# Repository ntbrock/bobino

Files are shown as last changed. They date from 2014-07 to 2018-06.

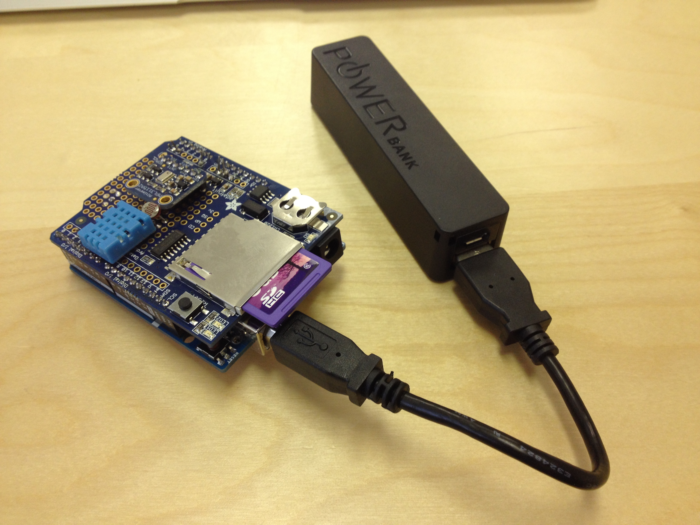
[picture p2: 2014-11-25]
Documentation/Bobino_Getting_Started_C.jpg

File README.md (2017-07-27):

BOBino
======

BOBino is an open source, educational, environmental sensor kit developed in Charleston, SC.  BOBino is built on Arduino open source hardware and intended to increase learning in electronics, data collection, and statistical analysis for students.

## Latest Release

Software: Version 1.6.1 (master)

Hardware: Version 1.6H (oshpark)

## Getting started quickly? 

Read the document "HOWTO Use Your Bobino.txt"

[HOWTO Use Your BOBino](https://github.com/ntbrock/bobino/blob/master/Documentation/HOWTO_Use_Your_Bobino.txt?raw=true)

## Announcing BOBino V1.6 at the South Carolina STEAM workshop

[View the July 2017 STEAM Workshop Presentation](https://github.com/ntbrock/bobino/blob/master/Documentation/BOBino%20STEAM%20Public%202017Jul.pptx?raw=true)

## Ready to compile the code yourself?

Latest codeset is in BOBino_Code_V1.6_2016Jun25, several Arduino libraries required: Narcoleptic, OneWire, DallasTemperature, RTClib

## Ready to build your own board?

Full schematic and PCB Layout avaialble on Autodesk's Circuits123

https://circuits.io/circuits/2376213-bobino-1-6h-environmental-data-logger-arduino-uno-half-shield

## Ready to order BOBino Kits or Arduino Shields for your classroom or workshop?

Email taylor.brockman@gmail.com with the Subject line: BOBino Order Information

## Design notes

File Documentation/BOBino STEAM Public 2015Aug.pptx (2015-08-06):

## BOBino 1.5 Environmental Logger Kit

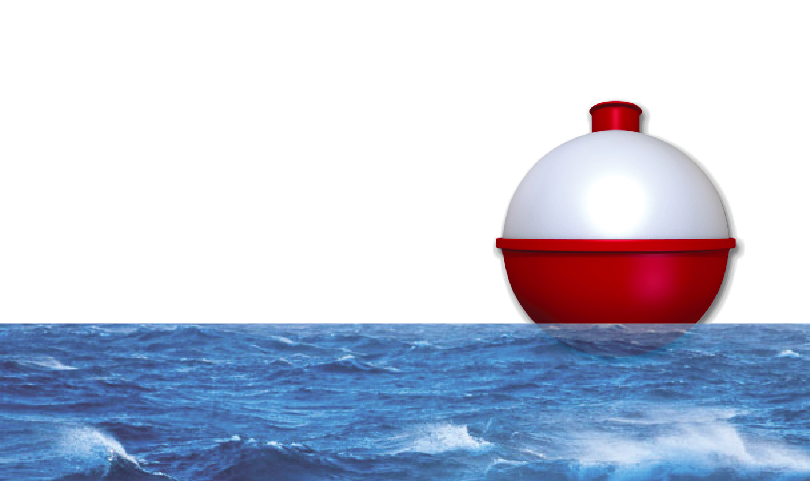
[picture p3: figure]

Taylor Brockman
2015-Aug-06

## NERD ALERT!

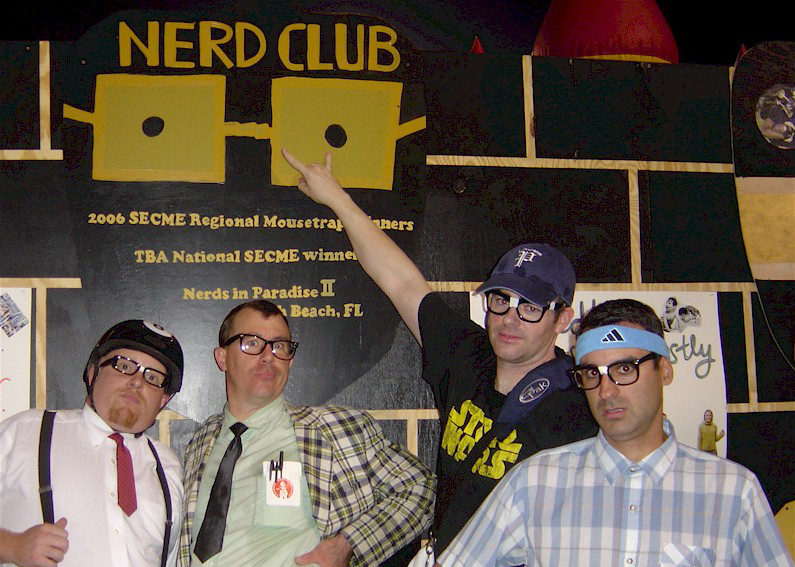
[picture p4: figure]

## NERD ALERT!

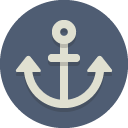
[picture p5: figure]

- New! Three Temperature Sensors!
- Open Source Code and Hardware
- Battery Powered, Durable, Cheap

## POP that tupperware open!

- STICKERS! (w/ QR Code)
- Arduino UNO plus “Shield”
- SD Memory Card
- 2 Temperature Sensor Wires
- Order Doesn’t Matter
- USB Battery and 2 Cables
- Power it up! Recharge anytime!

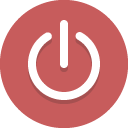
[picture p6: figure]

## We are LOGGIN The DATA!

- Default interval is 15 seconds
- Try covering up the Photo Sensor
- Try warming up a Temp Sensor
- Temp Sensors are submersible
- (Bubble Bubble Bubble)

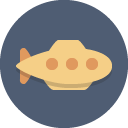
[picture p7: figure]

## Story Time & Fun pictureS

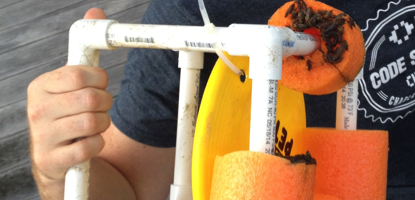
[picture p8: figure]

- Marina

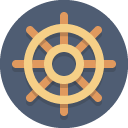
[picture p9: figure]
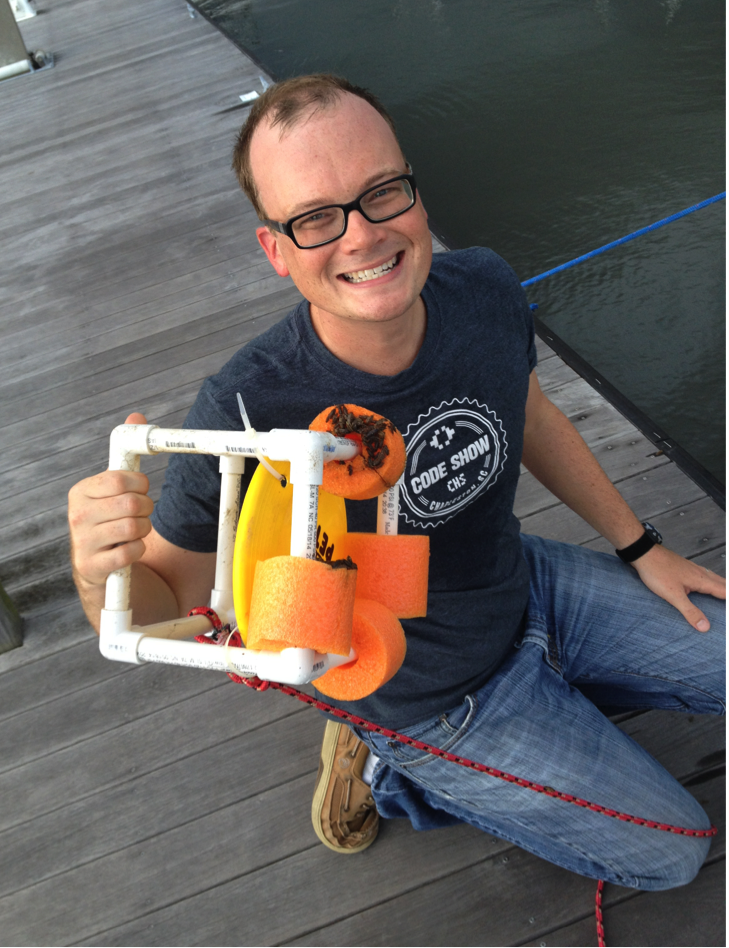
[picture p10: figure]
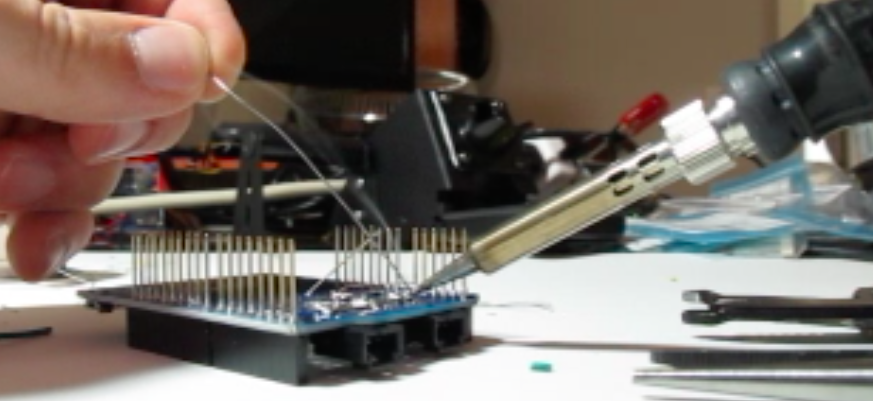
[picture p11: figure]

## Why BOBINO?

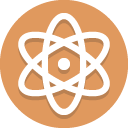
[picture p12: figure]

- Students need exposure to electronic data logging and statistical analysis and visualization.
- Commercial alternative is $1500
- Cha Ching!

## Let’s take a look ON OUR LAPTOPS

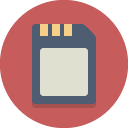
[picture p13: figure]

- SD Card can be plugged into any laptop or PC.
- DATA.CSV is “Comma Separated Values” that opens well in Excel.
- Change the Log Rate in CONFIG

## Let’s take a look ON OUR LAPTOPS

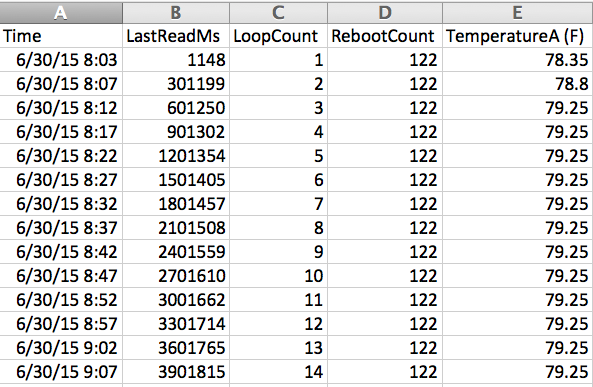
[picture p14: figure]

## Let’s take a look ON OUR LAPTOPS

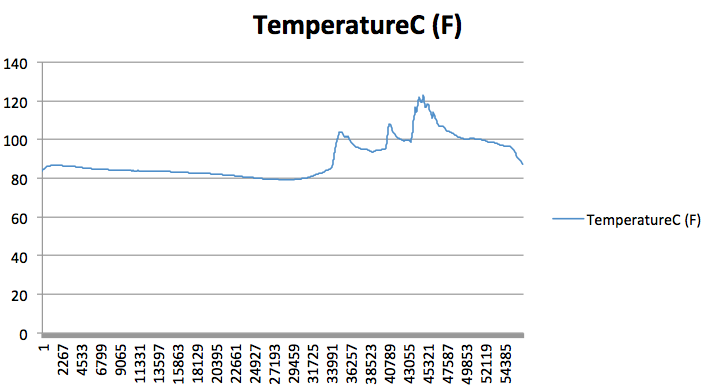
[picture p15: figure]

## Let’s take a look ON OUR LAPTOPS

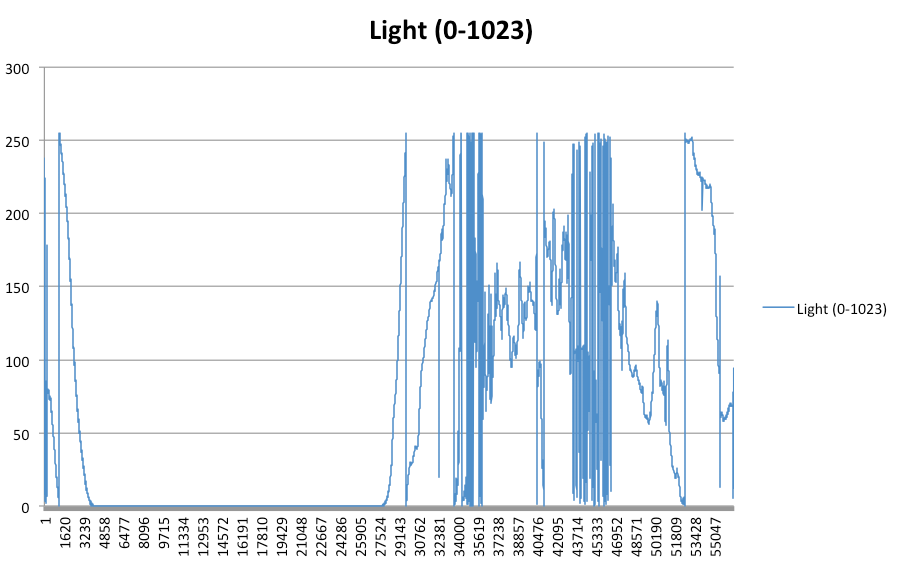
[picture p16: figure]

## Maybe it’s time to get a new fridge?

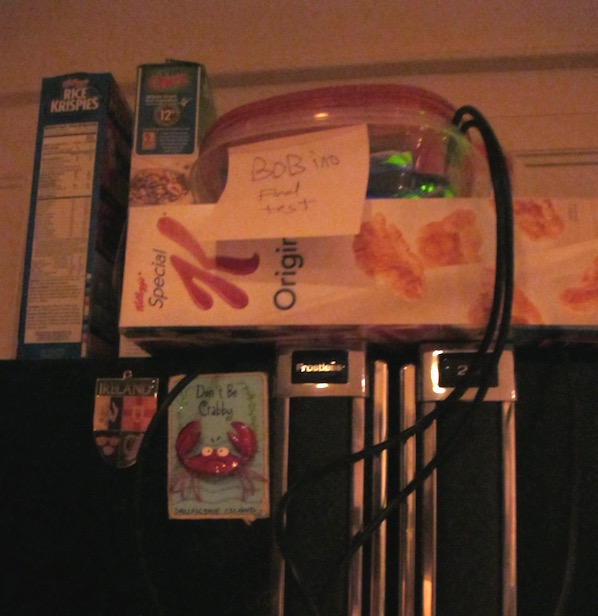
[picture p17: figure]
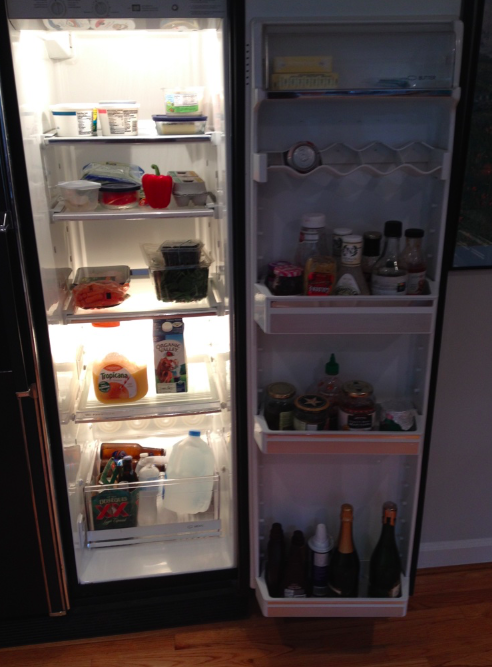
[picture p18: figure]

## Maybe it’s time to get a new fridge?

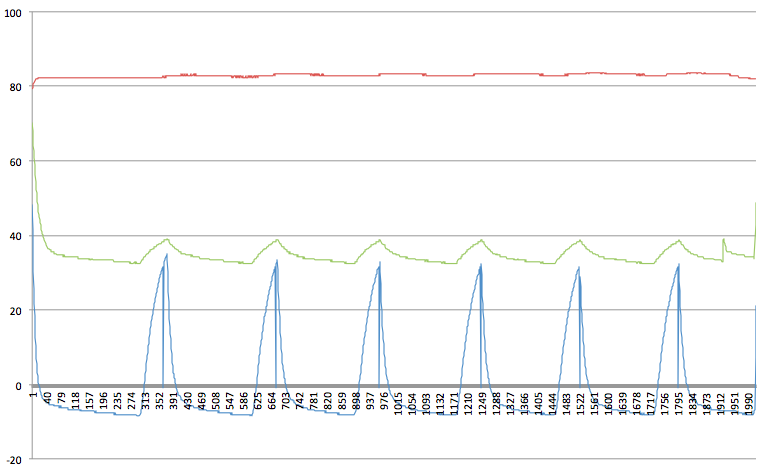
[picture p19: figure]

Morning Juice!

## Experiment IDEAS

- Refrigerator Performance
- Water Heating via Solar Radiance
- Air –vs– Water Temperature Diff
- Solar Day Length
- Cloud Cover –vs– Temperature
- Air Conditioner Thermostat Accuracy

## For the Experts

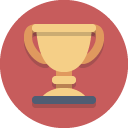
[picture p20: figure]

- All Source Code is available!
- Use the Arduino Programmer, Free Download!
- Add More Hardware, Change Shields, Increase the Battery Size
- Ocean or Sky is the limit!

## BOBino 1.5 Environmental Logger Kit

Taylor Brockman
2015-Aug-06

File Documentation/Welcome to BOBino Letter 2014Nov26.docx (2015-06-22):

November 26, 2014

Welcome to BOBino!

You are the proud custodian of a BOBino version 1.0 Arduino data sensor capture device, designed and assembled in Charleston, South Carolina, USA.

Your interest in the BOBino program helps create careers in Science, Technology, Engineering, Mathematics, and Software for bright, motivated students.

To get started with BoBinfo, assemble the unit, power it with the USB battery, then let it run for 5 minutes to collect readings! After that, remove the power, place the SD Card in any computer and open DATA.CSV in Microsoft Excel or a text editor to see all captured data points. Certain settings are configurable by editing the files in the CONFIG/ folder on the SD Card.

You can read a full getting started guide on the world wide web:

http://www.brockmanapprenticefoundation.org/Bobino/features.html

When you find a student who wants “more”, our Arduino source code is open, the BOBino can be reprogrammed and extended, and we are here to guide!

The Brockman Apprentice Foundation connects the brightest, hardest working students in the Carolinas to summer work / study programs. Learn more at:

http://www.brockmanapprenticefoundation.org/

Sincerely,
Taylor Brockman

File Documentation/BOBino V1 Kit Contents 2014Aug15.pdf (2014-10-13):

BOBino

V1 | | Taylor Brockman,

Maxwell

Tucker,

| | | | | Benson Robles
Kit
Contents | | 2014-‐Aug-‐15
Component | Vendor | Price
Each Qty | Ship
Rate Total | Description | URL
UNO | Adafruit | $24.95 | 5 | $0.00 $124.75 Arduino

Uno

R3

(Atmega328

-‐

assembled) http://www.adafruit.com/products/50 SD

Shield | Adafruit | $19.95 | 5 | $0.00 | $99.75 Adafruit

Assembled

Data

Logging

shield

for

Arduino[ID:1141] http://www.adafruit.com/product/1141 DHT11

Temp | Adafruit | $5.00 | 5 | $0.00 | $25.00 DHT11

basic

temperature-‐humidity

sensor

+

extras http://www.adafruit.com/products/386 Temp

Sensor | Adafruit | $9.95 | 5 | $0.00 | $49.75 MPL3115A2

-‐

I2C

Barometric

Pressure/Altitude/Temperature

Sensor[ID:1893] http://www.adafruit.com/product/1893 Photo

Sensor | Adafruit | $0.95 | 5 | $0.00 | $4.75 Photo cell (CdS

photoresistor)[ID:161] http://www.adafruit.com/product/161 USB

Battery | Adafruit | $14.95 | 5 | $0.00 | $74.75 USB Battery

Pack

-‐

2200

mAh

Capacity

-‐

5V

1A

Output http://www.adafruit.com/products/1959

SD

Card | Walmart | $4.83 | V7

2GB

SD

Card,

Secure

Digital

2

GB

Memory

Card

http://www.walmart.com/ip/V7-‐2GB-‐SD-‐Card-‐Secure-‐Digital-‐2-‐GB-‐Memory-‐Card/15172567

SD

Card

4G | Amazon | $5.75 | 6 | $0.00 | $34.50 SanDisk

SDSDB2L-‐004G-‐B35

http://www.amazon.com/gp/product/B002DS7NJI/ref=ox_sc_act_title_1?ie=UTF8&psc=1&smid=A3U5D1Y1DY YVD9
USB

B

Cable | Ebay | | | | 6" inch Black

USB

2.0

AB

Printer

-‐

Device

Cable

A-‐B
USB

AB

Cable | PCH
| Cables | $1.25 | 10 | $3.71 | $16.21 6 Inch USB

2.0

Type

A

Male

to

Type

B

Male

Cable

-‐

Black

http://www.pchcables.com/6inusb20tyma1.html

Tupperware | Publix | $1.00 | 5 | $0.00 | $5.00
Assembly
Labor | InnoLabs | $10 | 5 | $0.00 | $50.00

Total

Per

BOBino | | $96.89 | 5 | | $484.46 Grand

Total

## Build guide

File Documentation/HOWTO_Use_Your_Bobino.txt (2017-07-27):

HOWTO Use Your Bobino
BOBino V1.6 2017-Jul-27

0) BOBino kit contents:

   BOBino Purple Shield
   Data Logger Shield
   Arduino UNO Base
   USB Battery
   USB Square Cable
   USB Tiny Cable (for recharging battery)
   Two Temperature Probes
   Waterproof enclosure (Tupperware or Ziplock)

1) Assemble the unit:

A. Combine the shields: BOBino on top, Data Logger shield in the middle, Arduino UNO on the bottom.

B. Connect the temperature probes into Temp 1 and Temp 3, the plug will clip in with the clip facing up.

C. Place an SD Card Chip into Data Logger shield. If the card is blank, the first time BOBino boots up, it will write a new DATA.CSV file and create a CONFIG directory.

D. Plus the USB Power cable with the square end into the Arduino Uno, then plug the rectangular end into the USB Battery.

E. The unit takes approximately 5 seconds to boot up, initialize the SD card and begin taking readings!

F. Be sure that when you mount the BOBino into its waterproof case the photo sensor can see the sunlight and is not upside down.  I like to mount one temperature probe in the air and the other temperature probe into the water.

2) Let the Unit Run for 3 minutes 

The default sample rate is 1 reading per minute.

3) Unplug the Power and Read the SD card with a computer.

Remove the SD Card, and plug into any laptop or computer with an SD Card Reader.

On the disk, you will see a file called 'DATA.CSV', example contents:

Time,Temperature (F),Humidity,Pressure (in Hg),Light (Raw value 0-1023),Light (qualitative descriptor)
2000/1/1 0:0:0,74.19,47.00,30.05,316,bright
2014/9/5 16:27:0,74.75,47.00,30.05,323,bright
2014/9/5 16:27:59,74.64,47.00,30.05,321,bright
2014/9/5 16:28:59,74.75,47.00,30.05,319,bright
2014/9/5 16:29:59,74.97,47.00,30.06,338,bright
2014/9/5 16:30:59,75.09,47.00,30.05,326,bright

4) Reconfigure to your settings!

Adjust the settings on the Bobino is easy, simply edit the files in the CONFIG/ directory on the SD Card.

Edit The following files to set Configuration: 
   CONFIG/TEMP.TXT -- Set Temperature Units to F or C
   CONFIG/TIME.TXT -- Set Time Sleep Interval in minutes
   CONFIG/ALT.TXT -- Set Altitude Units and Activate
   CONFIG/RTCSET.TXT -- Set To the current calendar information to adjust system time.
   CONFIG/_RTCSET.TXT -- Example RTC File to make clock setting easy.

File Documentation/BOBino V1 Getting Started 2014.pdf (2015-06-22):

12/4/2014 | BOBino - Getting Started

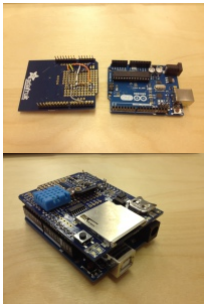
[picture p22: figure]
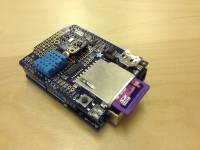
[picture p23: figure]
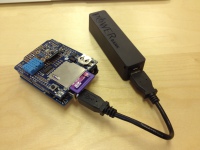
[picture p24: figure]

http://www.brockmanapprenticefoundation.org/Bobino/features.html | 1/3

# Getting Started with your BOBino

BOBino V1 2014-Sep-01

# 1) Assemble the BOBino:

A. The Sensor Shield attaches on top of the Arduino Uno

(Documentation/Bobino_GettingStarted_A.jpg) (http://www.brockmanapprenticefoundation.org/Bobino/Documentation/Bobino_GettingStarted_A.jpg)

(Documentation/Bobino_GettingStarted_A2.jpg) (http://www.brockmanapprenticefoundation.org/Bobino/Documentation/Bobino_GettingStarted_A2.jpg)

B. The SD Card is placed in the SD Card Slot of the sensor shield

(Documentation/Bobino_GettingStarted_B.jpg) (http://www.brockmanapprenticefoundation.org/Bobino/Documentation/Bobino_GettingStarted_B.jpg)

C. The Short USB Power cable is plugged into the battery, then plugged into the Arduino Uno

(Documentation/Bobino_GettingStarted_C.jpg) (http://www.brockmanapprenticefoundation.org/Bobino/Documentation/Bobino_GettingStarted_C.jpg)

http://www.brockmanapprenticefoundation.org/Bobino/features.html | 2/3
D. The unit takes approximately 10 seconds to boot up, initialize the SD card and begin taking readings!

# 2) Let the BOBino Run for 3 minutes

The default sample rate is 1 reading per minute.

# 3) Unplug the Power and Read the SD card with a

computer.

Remove the SD Card, and plug into any laptop or computer with an SD Card Reader.

On the disk, you will see a file called 'DATA.CSV', example contents:

Time,Temperature (F),Humidity,Pressure (in Hg),Light (Raw value 0-1023),Light ( qualitative descriptor)
2000/1/1 0:0:0,74.19,47.00,30.05,316,bright
2014/9/5 16:27:0,74.75,47.00,30.05,323,bright
2014/9/5 16:27:59,74.64,47.00,30.05,321,bright 2014/9/5 16:28:59,74.75,47.00,30.05,319,bright 2014/9/5 16:29:59,74.97,47.00,30.06,338,bright 2014/9/5 16:30:59,75.09,47.00,30.05,326,bright

# 4) Reconfigure to your settings!

Adjust the settings on the BOBino is easy, simply edit the files in the CONFIG/ directory on the SD Card.

When the BOBino recognizes a new SD card, it creates the CONFIG/ directory and automatically creates the below sample files.

Edit The following files to set Configuration:

CONFIG/TEMP.TXT -- Set Temperature Units to F or C
CONFIG/TIME.TXT -- Set Time Sleep Interval in minutes
CONFIG/ALT.TXT -- Set Altitude Units and Activate
CONFIG/RTCSET.TXT -- Set To the current calendar information to adjust system time. CONFIG/_RTCSET.TXT -- Example RTC File to make clock setting easy.

# 5) Adjust the Time Clock

The BOBino clock will need to be updated to your local time on first installation or whenever the clock battery becomes disconnected.

To set the clock, create a file on the SD card with the name: CONFIG/RTCSET.TXT with the contents:

2014 09 01 15 00 00;

http://www.brockmanapprenticefoundation.org/Bobino/features.html | 3/3

The above example would set the clock to the year 2014, the month of September, the first day of the month, 3PM in the afternoon.

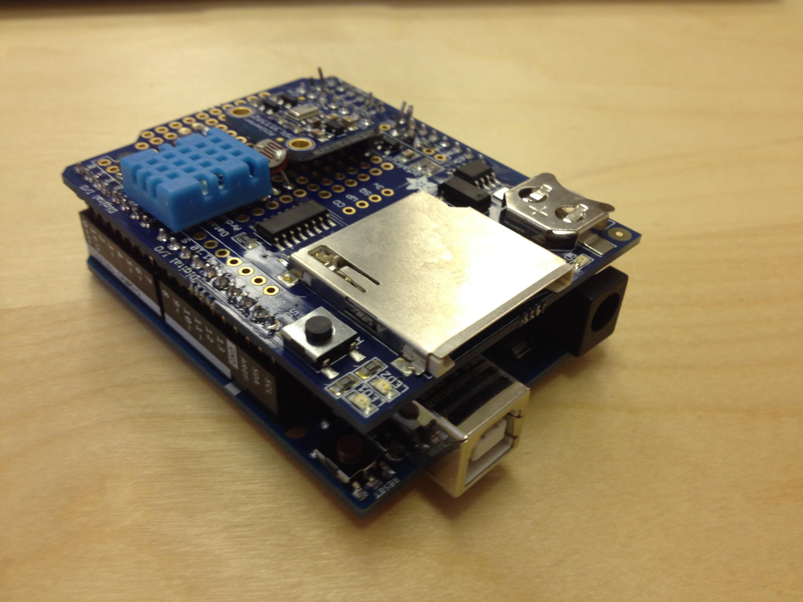
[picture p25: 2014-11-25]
Documentation/Bobino_GettingStarted_A2.jpg

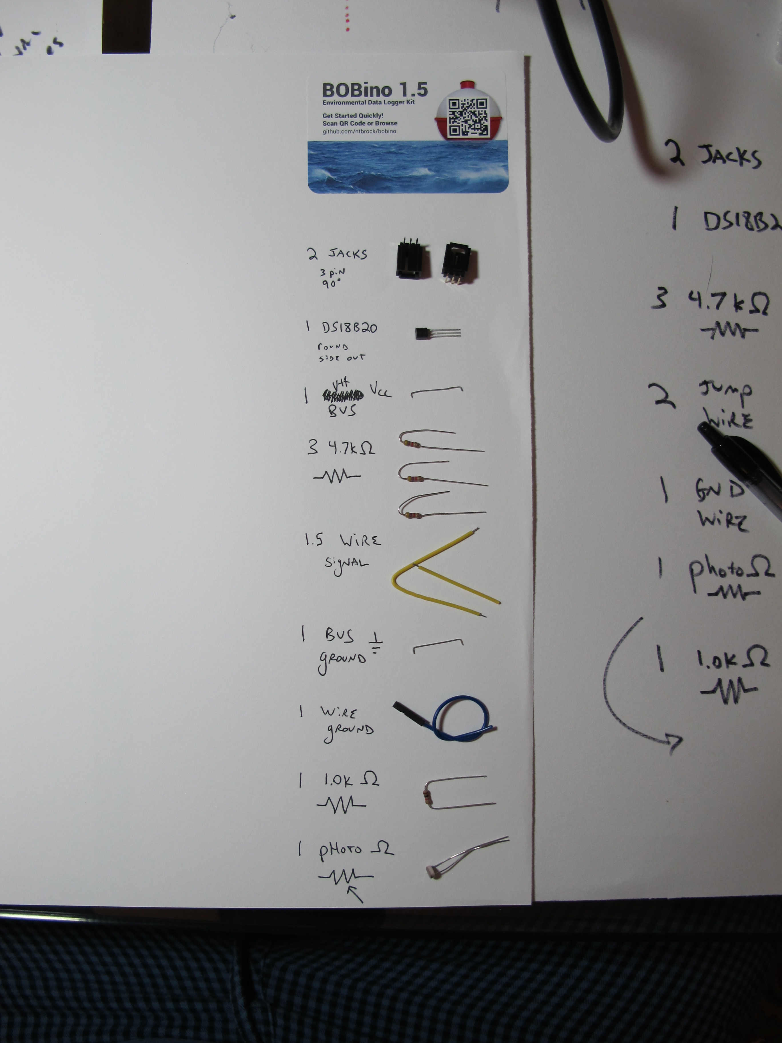
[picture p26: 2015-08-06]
Documentation/ConstructionV1.5/2015-07-19 10.06.52.jpg

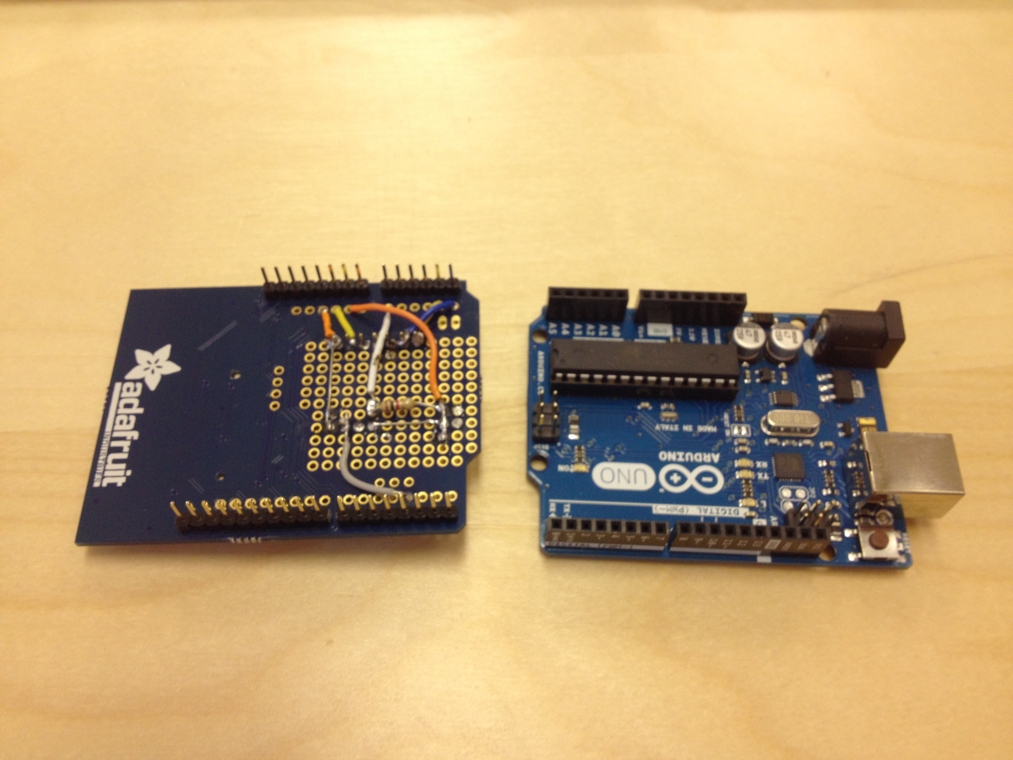
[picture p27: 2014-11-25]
Documentation/Bobino_GettingStarted_A.jpg

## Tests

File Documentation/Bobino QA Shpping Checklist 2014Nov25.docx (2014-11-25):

Bobino QA Checklist

2014-Nov-25

Test / Provisioning Steps:

- Physically mount SD Shield to Arduino, Clear of DIP IC

- RTC Clock Battery Installed

- USB Battery Charged

- Arduino Flashed via Arduno Studio w/ Github package.

- Arduino Boots, Serial Monitor OK

- SD Card Initialized, CONFIG folder, DATA.CSV file create

- _RTCSET.txt Clock Initialization

- Check Data.csv created and populated.

- Let it run for 5 mins, logging data

- All Sensors record values

- Temperature / Humidity / Light levels make sense

Shipped Package Contents:

- Tupperware

- USB B Cable

- USB A Cable

- USB Battery

- Electrostatic Bag

- Arduino (Programmed)

- BobIno Shield w/ RTC Clock Battery

- SD Card (Initialized)

- QA checklist / Quick start instructions

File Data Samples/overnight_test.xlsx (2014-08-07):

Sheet: overnight_test
2014-07-21 | 26.94 | 40 | 30.02 | -26.94 | 412 | bright | 80.492
2014-07-21 | 26.94 | 40 | 30.02 | -27.81 | 415 | bright | 80.492
2014-07-21 | 26.94 | 40 | 30.02 | -28.56 | 439 | bright | 80.492
2014-07-21 | 26.94 | 39 | 30.02 | -28.62 | 434 | bright | 80.492
2014-07-21 | 27 | 39 | 30.02 | -28.87 | 409 | bright | 80.6
2014-07-21 | 27 | 40 | 30.02 | -29.19 | 433 | bright | 80.6
2014-07-21 | 27 | 40 | 30.02 | -28.75 | 424 | bright | 80.6
2014-07-21 | 27 | 39 | 30.02 | -28.75 | 435 | bright | 80.6
2014-07-21 | 27 | 39 | 30.02 | -29.06 | 403 | bright | 80.6
2014-07-21 | 27 | 40 | 30.02 | -28.81 | 429 | bright | 80.6
2014-07-21 | 27 | 40 | 30.02 | -29.25 | 396 | bright | 80.6
2014-07-21 | 27.06 | 39 | 30.03 | -29.56 | 416 | bright | 80.708
2014-07-21 | 27.06 | 39 | 30.03 | -29.37 | 411 | bright | 80.708
2014-07-21 | 27.06 | 40 | 30.03 | -29.62 | 399 | bright | 80.708
2014-07-21 | 27.06 | 39 | 30.02 | -29 | 415 | bright | 80.708
2014-07-21 | 27.06 | 39 | 30.03 | -29.75 | 411 | bright | 80.708
2014-07-21 | 27.06 | 39 | 30.03 | -29.56 | 442 | bright | 80.708
2014-07-21 | 27.06 | 39 | 30.03 | -29.25 | 411 | bright | 80.708
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

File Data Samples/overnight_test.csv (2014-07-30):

7/21/2014 15:22 | 26.94 | 40 | 30.02 | -26.94 | 412 | bright
7/21/2014 15:23 | 26.94 | 40 | 30.02 | -27.81 | 415 | bright
7/21/2014 15:25 | 26.94 | 40 | 30.02 | -28.56 | 439 | bright
7/21/2014 15:27 | 26.94 | 39 | 30.02 | -28.62 | 434 | bright
7/21/2014 15:29 | 27 | 39 | 30.02 | -28.87 | 409 | bright
7/21/2014 15:31 | 27 | 40 | 30.02 | -29.19 | 433 | bright
7/21/2014 15:33 | 27 | 40 | 30.02 | -28.75 | 424 | bright
7/21/2014 15:35 | 27 | 39 | 30.02 | -28.75 | 435 | bright
7/21/2014 15:37 | 27 | 39 | 30.02 | -29.06 | 403 | bright
7/21/2014 15:39 | 27 | 40 | 30.02 | -28.81 | 429 | bright
7/21/2014 15:41 | 27 | 40 | 30.02 | -29.25 | 396 | bright
7/21/2014 15:43 | 27.06 | 39 | 30.03 | -29.56 | 416 | bright
7/21/2014 15:45 | 27.06 | 39 | 30.03 | -29.37 | 411 | bright
7/21/2014 15:47 | 27.06 | 40 | 30.03 | -29.62 | 399 | bright
7/21/2014 16:04 | 27.06 | 39 | 30.02 | -29 | 415 | bright
7/21/2014 16:06 | 27.06 | 39 | 30.03 | -29.75 | 411 | bright
7/21/2014 16:08 | 27.06 | 39 | 30.03 | -29.56 | 442 | bright
7/21/2014 16:10 | 27.06 | 39 | 30.03 | -29.25 | 411 | bright
7/21/2014 16:12 | 27.06 | 39 | 30.02 | -28.87 | 435 | bright
7/21/2014 16:14 | 27.06 | 39 | 30.02 | -28.62 | 432 | bright
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

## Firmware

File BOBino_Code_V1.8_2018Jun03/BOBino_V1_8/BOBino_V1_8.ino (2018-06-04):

/***********************************************************
 * BOBino V1.8: Arduino Sensor Platform by Max Tucker, Taylor Brockman
 * Full documentation, including a parts list, can be found at https://github.com/ntbrock/bobino
 *
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
 * Change Log:
 *  Brockman 2018-Jun-03: 1.8 - OLED Screen capabilities, removed Narcoleptic library + photo qual
 *  Brockman 2017-Jul-23: 1.6.1 - Photo reading into int instead of byte to stabilize values
 *  Brockman 2016-Jul-17: 1.6 - Final Flash, Turned new date into Macro
 *  Brockman 2016-Jun-25: Code Revision, testing, and final OSH Park order for printed boards.
 *  Brockman 2015-Jul-19: Official Version loaded onto 30 BOBino's, final analogRead timing fix.
 *  Brockman 2015-Jun-18: Inclusion of the DallasTemperature and Onewire libs
 *      Dedpopulated the MPL and DHT to opt for 3 temp sensors!
 *  Brockman 2014-Sep-02: Defaulted configurations for time so RAW SD card works
 *  Brockman 2014-Sep-02: Serial writing for debugging added
 *  Brockman 2014-Sep-02: Memory optimization http://forum.arduino.cc/index.php?topic=163307.0
 */


// Flash Size must been < 30720 bytes, else you get the verification error in avrdude.

#include <Wire.h>

// 2015-Jun - Replaced the components with simple DS18B20 one-wire temperature sensors
#include <OneWire.h>
#include <DallasTemperature.h>

// SD Card and Sleep
#include <SPI.h>
#include <SD.h>
#include <avr/sleep.h>

#include <RTClib.h> //Available from https://github.com/adafruit/RTClib
//#include <Narcoleptic.h> //microcontroller sleep library. Available at https://code.google.com/p/narcoleptic/downloads/detail?name=Narcoleptic_v1a.zip

//http://www.arduino.cc/en/Tutorial/EEPROMWrite
#include <EEPROM.h>

// 1.8 Include display driver
//#include <U8g2lib.h>
#include <SSD1306Ascii.h>
#include <SSD1306AsciiAvrI2c.h>

#define I2C_ADDRESS 0x3C
// Define proper RST_PIN if required.
#define RST_PIN -1

SSD1306AsciiAvrI2c oled;

//http://www.instructables.com/id/two-ways-to-reset-arduino-in-software/step2/using-just-software/
void(* resetFunc) (void) = 0; //declare reset function @ address 0


#define RTCSET_DATE "2018 06 04 09 30 00;"

#define DEFAULT_SLEEP_SECONDS 15


// Enable up to three differene one wire busses
// This avoids identifying each one-wire by hex id.
#define ONE_WIRE_BUS_A   2
#define ONE_WIRE_BUS_B   3
#define ONE_WIRE_BUS_C   4

// Analog Voltage based Light Sennsor
#define PHOTO_PIN A0

RTC_DS1307 RTC;
OneWire oneWireA(ONE_WIRE_BUS_A);
OneWire oneWireB(ONE_WIRE_BUS_B);
OneWire oneWireC(ONE_WIRE_BUS_C);

DallasTemperature sensorsA(&oneWireA);
DallasTemperature sensorsB(&oneWireB);
DallasTemperature sensorsC(&oneWireC);

//U8G2_SSD1306_128X64_NONAME_1_HW_I2C u8g2(U8G2_R0, U8X8_PIN_NONE); // All Boards without Reset of the Display


char temp = 'F';
char alt = 'F';
short sleepSeconds = DEFAULT_SLEEP_SECONDS;

#define CSV ","
#define DATA_FILENAME "data.csv"
#define RTC_FILENAME "config/rtcset.txt"
#define CONFIG_DIR "config"
#define TIME_FILENAME "config/sleepsec.txt"
#define TEMP_FILENAME "config/temp.txt"
#define ALT_FILENAME "config/alt.txt"
#define RTC_EXAMPLE "config/_rtcset.txt"
#define README_FILENAME "BOBino.txt"

#define LOW_MEMORY_FREE_REBOOT_THRESHOLD 350
#define EEPROM_ADDR_Reset_Counter 0

//https://gist.github.com/ntbrock/4d0bec130f943861a0ba
byte resetCount = 0;
byte freeMemCount = 0;
uint16_t freeMem() {
  char top;
  extern char *__brkval;
  extern char __bss_end;
  int freeMem = __brkval ? &top - __brkval : &top - &__bss_end;

  if ( freeMemCount % 100 == 0 ) { 
  Serial.print(F("Debug: ["));
  Serial.print( freeMemCount, DEC );
  Serial.print(F("] SRAM Free: (Resetting at 350 free with NO warning)  "));
  Serial.println( freeMem );
  }
  freeMemCount++;
  
  if ( freeMem < LOW_MEMORY_FREE_REBOOT_THRESHOLD ) { 
   Serial.print(F("FATAL: SRAM Free: (RESETTING NOW)  "));
    Serial.println( freeMem, DEC );
    Serial.flush();
    delay(50);
    resetFunc();  //call reset - no room for death squawk
  }
}

char oledBuffer12[12] = "       ";

void setup() {

  Serial.begin(9600);
  
  Serial.println(F("BOBino V1.8 ==[setup]===="));
  freeMem();
  countResets();
  delay(50);

#if RST_PIN >= 0
  oled.begin(&Adafruit128x64, I2C_ADDRESS, RST_PIN);
#else // RST_PIN >= 0
  oled.begin(&Adafruit128x64, I2C_ADDRESS);
#endif // RST_PIN >= 0

  oled.setFont(X11fixed7x14); // TimesNewRoman16);
  oled.clear();
  oled.println(F("BOBino V1.8"));

  //timestamp from rtc
  DateTime now = RTC.now();

  oled.print(now.year(), DEC);
  oled.print('/');
  oled.print(now.month(), DEC);
  oled.print('/');
  oled.print(now.day(), DEC);
  
  oled.println();
  if ( now.hour() < 10 ) { oled.print("0"); }
  oled.print(now.hour(), DEC);
  oled.print(':');
  if ( now.minute() < 10 ) { oled.print("0"); }
  oled.print(now.minute(), DEC );
  oled.print(':');
  if ( now.second() < 10 ) { oled.print("0"); }
  oled.println(now.second(), DEC);

  //This is the chipselect pin, change based on SD shield documentation.
  if ( ! SD.begin(10) ) { 
    oled.println(F("NO SD CARD"));
    Serial.println(F("FATAL: Unable to begin SD Card."));
    Serial.flush();
    deathFlash();
  } else {     

    sprintf(oledBuffer12, "%d Resets", (int)resetCount);
    oled.println(oledBuffer12);


    sensorsA.begin();
    sensorsB.begin();
    sensorsC.begin();
    delay(50);

    Wire.begin();
    RTC.begin();

    delay(50);
    configure();

    createHeader();
    RTC_set(); 

    sensorsA.setResolution(10);
    sensorsB.setResolution(10);
    sensorsC.setResolution(10);

    Serial.print(F("BOBino V1.8 ==[loop]====  Go! Loop sleeps seconds: "));
    Serial.println(sleepSeconds);
  }
}

int loopCount = 0;
long lastReadMs = -1;

void loop(){
  loopCount += 1;
  freeMem();

  lastReadMs = millis();// + Narcoleptic.millis();
  DateTime now = RTC.now();

  // Acquire All readings
  sensorsA.requestTemperatures(); 
  sensorsB.requestTemperatures(); 
  sensorsC.requestTemperatures(); 
  analogRead(PHOTO_PIN); // discard first reading, use 2nd
  // Data capacity fix for Photo fluctuation
  int photoRead = analogRead(PHOTO_PIN);
    
  // Acquisition Time off temperature sensors
  delay(650);

  float tempA = -1;
  float tempB = -1;
  float tempC = -1; 
  
  if(temp=='f'||temp=='F'){
    tempA = sensorsA.getTempFByIndex(0);
    tempB = sensorsB.getTempFByIndex(0);
    tempC = sensorsC.getTempFByIndex(0);
  } else {
    tempA = sensorsA.getTempCByIndex(0);
    tempB = sensorsB.getTempCByIndex(0);
    tempC = sensorsC.getTempCByIndex(0);
  }

  // 32.00 indicates error, missing device on bus
  if ( tempA == 32.00 ) { tempA = -1; }
  if ( tempB == 32.00 ) { tempB = -1; }
  if ( tempC == 32.00 ) { tempC = -1; }

  File data=SD.open(DATA_FILENAME, FILE_WRITE);
  if ( data ) { 

    timestamp(data, now);
    data.print(CSV);
    data.print(lastReadMs, DEC);
    data.print(CSV);
    data.print(loopCount, DEC);
    data.print(CSV);
    data.print(resetCount, DEC);
    data.print(CSV);
    data.print(tempA, 2);
    data.print(CSV);
    data.print(tempB, 2);
    data.print(CSV);
    data.print(tempC, 2);
    data.print(CSV);
    data.print(photoRead, DEC);
    data.println();
    data.close();

    // Also debug to serial console
    timestampSerial(now);
    Serial.print(CSV);
    Serial.print(lastReadMs, DEC);
    Serial.print(CSV);
    Serial.print(loopCount, DEC);
    Serial.print(CSV);
    Serial.print(resetCount, DEC);
    Serial.print(CSV);
    Serial.print(tempA, 2);
    Serial.print(CSV);
    Serial.print(tempB, 2);
    Serial.print(CSV);
    Serial.print(tempC, 2);
    Serial.print(CSV);
    Serial.print(photoRead, DEC);
    Serial.print(CSV);
    Serial.println();
    Serial.flush();
  } else { 
    Serial.print(F("FATAL: Unable to write to SD, File: "));
    Serial.println(DATA_FILENAME);
    Serial.flush();
    deathFlash();
  }

  // Write to OLED Screen
  oled.clear();
  char oledBuffer[12] = "       ";
  sprintf(oledBuffer, "Temp1  %d   %d", (int)tempA, loopCount);
  oled.println(oledBuffer);

  sprintf(oledBuffer, "Temp2  %d", (int)tempB);
  oled.println(oledBuffer);

  sprintf(oledBuffer, "Temp3  %d", (int)tempC);
  oled.println(oledBuffer);
 
  sprintf(oledBuffer, "Photo  %d", (int)photoRead);
  oled.println(oledBuffer);
 
  sleep();

}

// Death Flash
void deathFlash() { 
  cli();
  sleep_enable();
  sleep_cpu();
}


void createHeader(){ //This function creates a header at the top of the data.csv file.
  if(SD.exists(DATA_FILENAME) == false){  //only creates header if file doesn't exist
    File data=SD.open(DATA_FILENAME, FILE_WRITE);
    data.print("Time");
    data.print(CSV);
    data.print("LastReadMs");
    data.print(CSV);
    data.print("LoopCount");
    data.print(CSV);
    data.print("RebootCount");
    data.print(CSV);
    if(temp=='f'||temp=='F'){
      data.print(F("TemperatureA (F)"));
    }else{
      data.print(F("TemperatureA (C)"));
    }
    data.print(CSV);
    if(temp=='f'||temp=='F'){
      data.print(F("TemperatureB (F)"));
    }else{
      data.print(F("TemperatureB (C)"));
    }
    data.print(CSV);
    if(temp=='f'||temp=='F'){
      data.print(F("TemperatureC (F)"));
    }else{
      data.print(F("TemperatureC (C)"));
    }
    data.print(CSV);
    data.print(F("Light (0-1023)"));
    data.println();
    data.close();
  }
  else{
    // File handle is refereshed with every loop, not held in memory.
    // data=SD.open("data.csv", FILE_WRITE);
  }
}

void timestamp(File data, DateTime &now){ //Current time is read from the RTC, and printed to the SD card.
  //timestamp from rtc
  data.print(now.year(), DEC);
  data.print('/');
  data.print(now.month(), DEC);
  data.print('/');
  data.print(now.day(), DEC);
  data.print(' ');
  if ( now.hour() < 10 ) { data.print("0"); }
  data.print(now.hour(), DEC);
  data.print(':');
  if ( now.minute() < 10 ) { data.print("0"); }
  data.print(now.minute(), DEC );
  data.print(':');
  if ( now.second() < 10 ) { data.print("0"); }
  data.print(now.second(), DEC);
}

void timestampSerial(DateTime &now){ //Current time is read from the RTC, and printed to the SD card.
  Serial.print(now.unixtime());
}


/**
 * Read the beginning of the EEPROM to get the number of resets and + 1.
 */
void countResets() {

  resetCount  = EEPROM.read(EEPROM_ADDR_Reset_Counter);
    Serial.print(F("Debug: Total Reset Count: "));
    Serial.println(resetCount);
  EEPROM.write(EEPROM_ADDR_Reset_Counter, resetCount+1);  
}


/**
 * Read the contents of the config folder on the SD card,
 * set memory config for data collection accordingly.
 */
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

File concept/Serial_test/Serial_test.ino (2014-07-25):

/***********************************************************
Early test of functionality over serial port
************************************************************/
#include <Wire.h>
#include <Adafruit_MPL3115A2.h> //Temperature/pressure sensor support. Available at https://github.com/adafruit/Adafruit_MPL3115A2_Library
#include <Narcoleptic.h> //microcontroller sleep library
#include <SD.h>
#include <DHT.h> //This library supports DHTxx sensors, in this case DHT11 temp/ humidity. Available from https://github.com/adafruit/DHT-sensor-library
#include <RTClib.h> //Available from https://github.com/adafruit/RTClib

//Adafruit_MPL3115A2 baro = Adafruit_MPL3115A2();
#define DHTPIN 3    // what pin the DHT is connected to
#define DHTTYPE DHT11 
DHT dht(DHTPIN, DHTTYPE);
int photo_pin = A0; //currently testing with photoresistor,connected to A0 and 5V, with 1kohm pulldown

RTC_DS1307 RTC;

//pins defined below are switches for unit conversions
int temp_pin=0 ;//C to F
int alt_pin=1 ;//meters to feet
int time_pin=2 ;//1 min intervals and 30 min intervals


void setup(){
  Serial.begin(9600); 

   Serial.print("Time");
  Serial.print(",");
  Serial.print("Temperature");
  Serial.print(",");
  Serial.print("Humidity");
  Serial.print(",");
  Serial.print("Pressure (in Hg)");
  Serial.print(",");
  Serial.print("Altitude (meters)");
  Serial.print(",");
  Serial.print("Light (Raw value 0-1023)");
  Serial.print(",");
  Serial.print("Light (qualitative descriptor");
  Serial.println();

  //baro.begin();
  dht.begin();
  Wire.begin();
  RTC.begin();
  
  pinMode(temp_pin, INPUT);
  pinMode(alt_pin, INPUT);
  pinMode(time_pin, INPUT);
}


void loop(){
  DateTime now = RTC.now();
  //float pascals=baro.getPressure();
  //float inHg=pascals/3386.389; 
  float degC=baro.getTemperature();
  float degF=degC*9/5+32;
  float altM=baro.getAltitude();
  float altFt=altM*3.28;

   //timestamp from rtc
  Serial.print(now.year(), DEC);
  Serial.print('/');
  Serial.print(now.month(), DEC);
  Serial.print('/');
  Serial.print(now.day(), DEC);
  Serial.print(' ');
  Serial.print(now.hour(), DEC);
  Serial.print(':');
  Serial.print(now.minute(), DEC);
  Serial.print(':');
  Serial.print(now.second(), DEC);
 
  Serial.print(",");
  if(digitalRead(temp_pin)==HIGH){
    Serial.print(degC);
  }else{
    Serial.print(degF);
  }
  Serial.print(",");
  Serial.print(dht.readHumidity()); //DHT uses "read" rather than "get." readTemperature is also available, but less accurate than other sensor
  Serial.print(",");
  Serial.print(inHg);
  Serial.print(",");
  if(digitalRead(alt_pin)==HIGH){
    Serial.print(altM);
  }else{
    Serial.print(altFt);
  }
  Serial.print(",");
  Serial.print(analogRead(photo_pin));
  Serial.print(",");
  //below prints qualitative descriptors of light intensity
  if(analogRead(photo_pin) < 10){
    Serial.print("dark");
  }else if(analogRead(photo_pin)<100){
    Serial.print("dim");
  }else if(analogRead(photo_pin)<300){
    Serial.print("light");
  }else if(analogRead(photo_pin)<600){
    Serial.print("bright");
  }else{
    Serial.print("very bright");
  }
  
  Serial.println();

  if(digitalRead(time_pin)==HIGH){
    Narcoleptic.delay(1800000-millis()%1000); //set to collect data every 30 minutes
  }else{
    Narcoleptic.delay(60000-millis()%1000); //set to collect data every minute
  }
}

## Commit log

2014-07-14 Examples of 2013 Project Solar Logger output
    [LOGGER00.CSV, LOGGER08.CSV]
2014-07-14 Updated code with full sensor support
    support for temperature, humidity, and pressure sensors, along with RTC
    integration. Currently untested.
2014-07-15 SD file creation change, switches to change units
    Changed file interfacing to prevent duplicate headers in log file. Added
    three switches in total, two to change units for temperature and
    altitude, and one to change collection interval from 1 to 30 min.
2014-07-18 Switched pressure sense libraries, added sample data
    [firstsample_pressureissues.csv]
2014-07-18 Fixed pressure issues and added working sample data
    [sample2_success.CSV]
2014-07-23 Wrote config file read test, added additional sample data
    [overnight_test.csv]
2014-07-30 fixed interval set function
    filename was too long, unsupported by arduino, thus causing it to hang
    on startup. 'intervalset' changed to 'time'
    [overnight_test.csv, overnight_test.xlsx]
2014-08-05 Changed header format, added some additional comments
    [2daydata.csv, overnight_test.xlsx]
2014-08-07 Final production commit!
    [overnight_test.xlsx]
2014-08-25 Arduino re-location
2014-09-03 Added BOBino SD Card sample content
    [DATA.CSV]
2015-08-06 STEAM Document commit
    [Vagabond Fridge.CSV, Vagabond Fridge.xlsx]
2016-06-25 Added BOBino v1.6 build and board
    [circuit.drl, circuit.gbl, circuit.gbo, circuit.gbs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]
2016-07-12 Added New fridge format
    [circuit.drl, circuit.gbl, circuit.gbo, circuit.gbs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]
2017-07-27 Uploaded dataset from STEAM 2017 workshop
    [BOBino_26Golfballs.csv, BOBino_Atistic.csv, BOBino_GreenSeaFoam.csv]
2018-06-03 Application Runs via windows arduino
2018-06-03 Builds but gives -196 temperature reads
2018-06-04 Official Pass at 1.8, in proper new directory name
    [circuit.drl, circuit.gbl, circuit.gbo, circuit.gbs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]
2018-06-04 Disabled Narcoleptic, staged addition of OLED library
2018-06-04 Print error message when no sd card

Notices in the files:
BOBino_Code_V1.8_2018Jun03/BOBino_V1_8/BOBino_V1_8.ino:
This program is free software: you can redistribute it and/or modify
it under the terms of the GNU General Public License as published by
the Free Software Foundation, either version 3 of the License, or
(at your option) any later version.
